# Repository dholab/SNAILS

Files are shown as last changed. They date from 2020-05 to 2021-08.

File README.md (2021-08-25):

# SNAILS v2.0
Since publishing, we have created a new version that is more mobile, efficient, and adaptable. This design also works with the more-common, upright Eppendorf pipette rather than the self-standing Ovation pipette. Please navigate to the SNAILS_v2 folder for the design.

SNAILS v2.0 assembly video: https://youtu.be/8Qm_oOv1cj8

# SNAILS v1.0
Slow Nucleic Acid Instrument for Long Sequences

SNAILS was created by Trent Prall and Emma Neumann. Its purpose is to improve ultralong read sequencing library preparation by reducing DNA shearing due to pipetting. 

preprint: https://www.biorxiv.org/content/10.1101/2020.09.18.302471v1

SNAILS v1.0 assembly video: https://youtu.be/rlQ-tXXK3FM

SNAILS v1.0 circuitry video: https://youtu.be/u-fqjHdVTUg

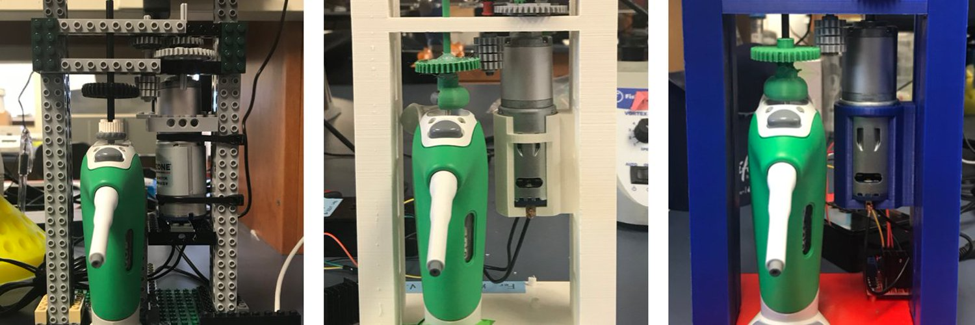
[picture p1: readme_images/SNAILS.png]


# Abstract
**Background** Oxford Nanopore Technologies’ instruments can sequence reads of great length. Long reads improve sequence assemblies by unambiguously spanning repetitive elements of the genome. Sequencing reads of significant length requires the preservation of long DNA template molecules through library preparation by pipetting reagents as slowly as possible in order to minimizing shearing. This process is time consuming and inconsistent at preserving read length as even small changes in volumetric flow rate can result in template shearing.

**Results** We have designed SNAILS (Slow Nucleic Acid Instrument for Long Sequences), a 3D-printable instrument that automates slow pipetting of reagents used in long read library preparation for Oxford Nanopore sequencing. Across six sequencing libraries, SNAILS preserved more reads exceeding one hundred kilobases in length and increased the average read length of its libraries over manual slow pipetting.

**Conclusions** SNAILS is a low-cost, easily deployable solution for improving sequencing projects that require reads of significant length. By automating the slow pipetting of library preparation reagents, SNAILS both increases the consistency and throughput of long read Nanopore sequencing.

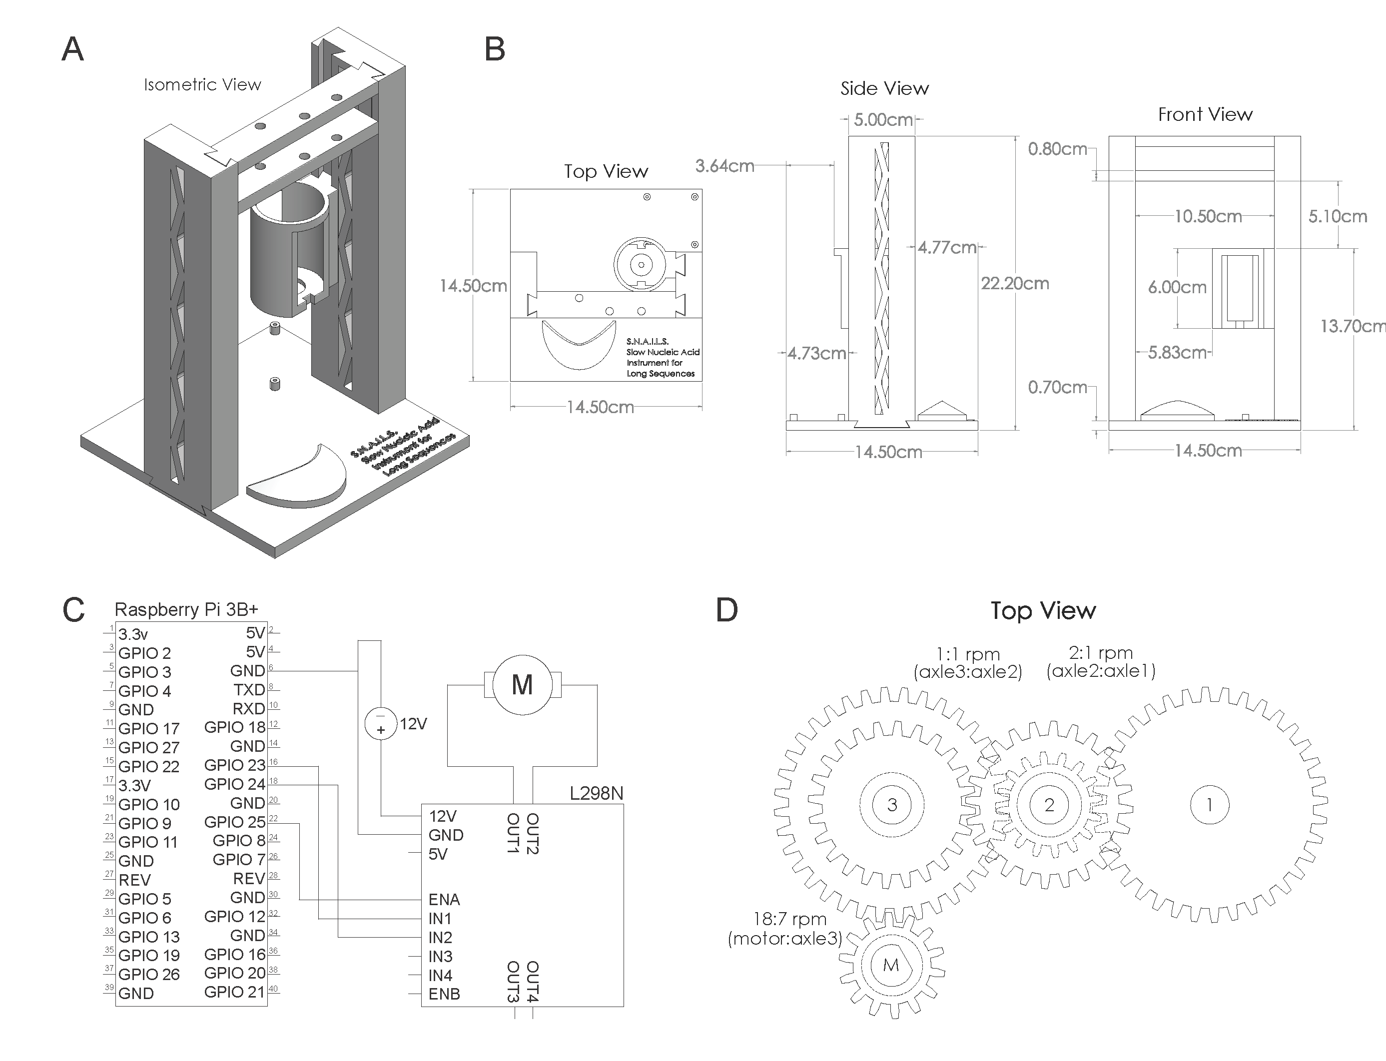
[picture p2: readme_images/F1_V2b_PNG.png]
F1_V2b_PNG


# Parts List
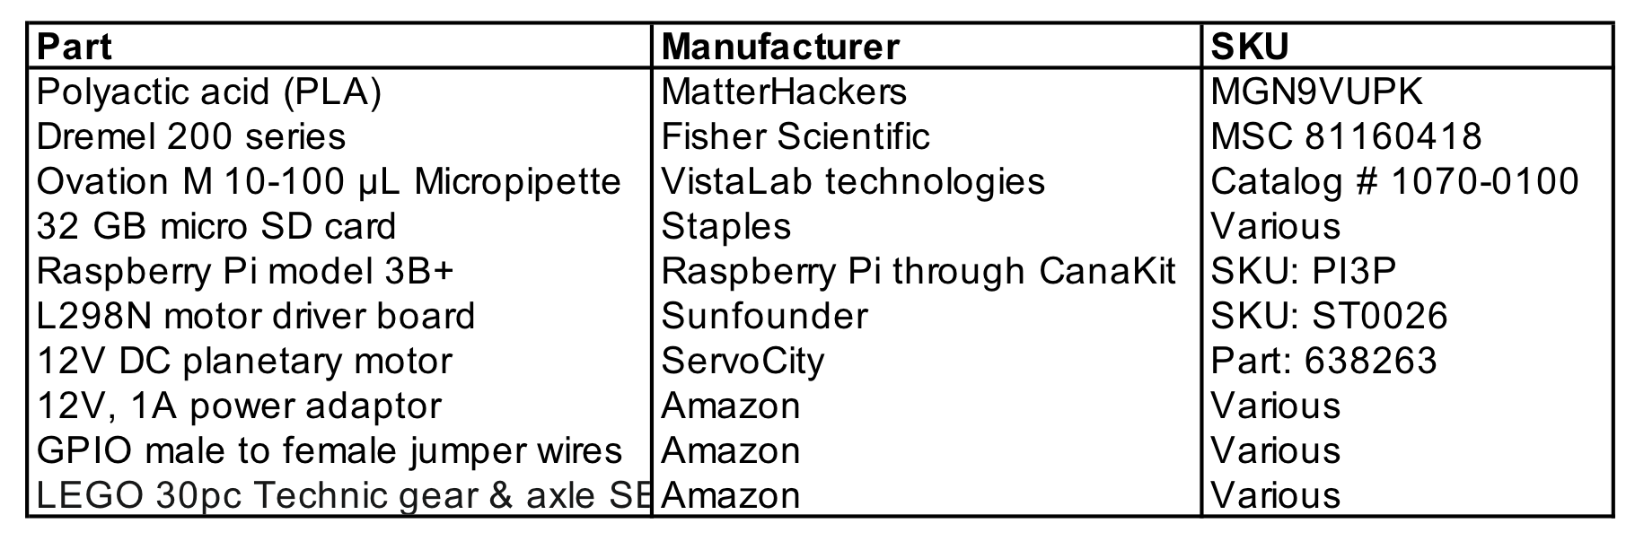
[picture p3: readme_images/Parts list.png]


# Printing Instructions
We used Ultimaker 3, S3, and S5 3D printers with the Ultimaker Cura program (https://ultimaker.com/software/ultimaker-cura). We recommend PLA for the printing material with the point set to 0.2 mm and infill at 20% for all the pieces. For the base, motor holder, and bridge, support material needs to be included, and changing the support density to 25 for a smoother print job is recommended. Additionally, we recommend that the base is printed on a separate build plate than the other pieces because it is so much thinner and by separating the pieces you increase the chances of a successful print job. More detailed, step-by-step printing instructions are directly below.

## Instructions for 3D printing SNAIL robot using an Ultimaker Cura
1. Connect to printer – this must be the first step because any and all settings altered will change anytime the printer is changed. You can connect to the printer through an IP address or network connection; follow the instructions on the screen. I used an Ultimaker 3 for the base and an Ultimaker S5 for the other four pieces; however, you can use any combination to print all the pieces. If you use a printer smaller than an S5 make sure it can still fit the towers and do not print all four pieces together. When printing multiple pieces at once, make sure the heights are about equal and the plate isn’t too full (Fig. 4 is the most crowded a plate should be). The base should be printed separate the other pieces because it is so much thinner than the others to increase the chances of a successful print. Once the printer is selected your screen should look like this:
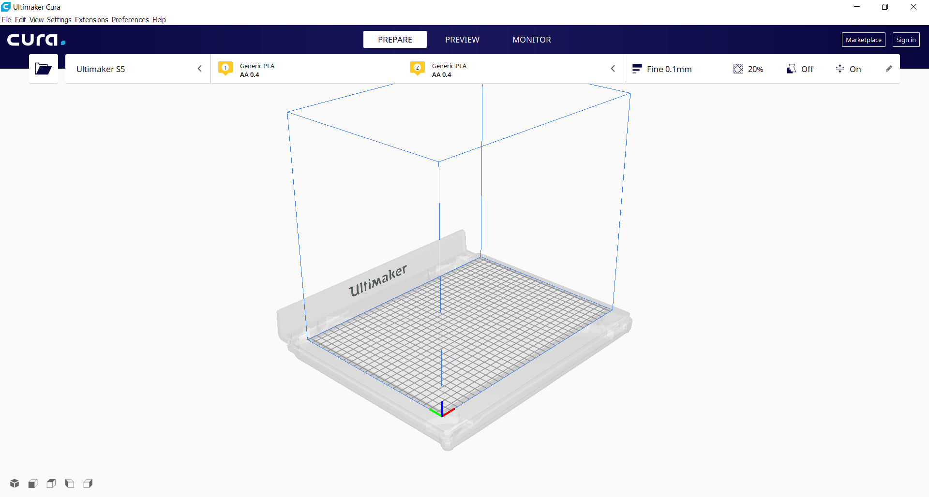
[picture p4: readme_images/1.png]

2. Open a file folder with all the STL files and drag those files into Cura onto the schematic of the printer.
3. Click on the part(s) and use the toolbar along the left side to rotate and move the parts (the next two pictures depict these movements) so that it lies flat on the printer and reduces support material. The pieces should be oriented as depicted below to produce the best prints.
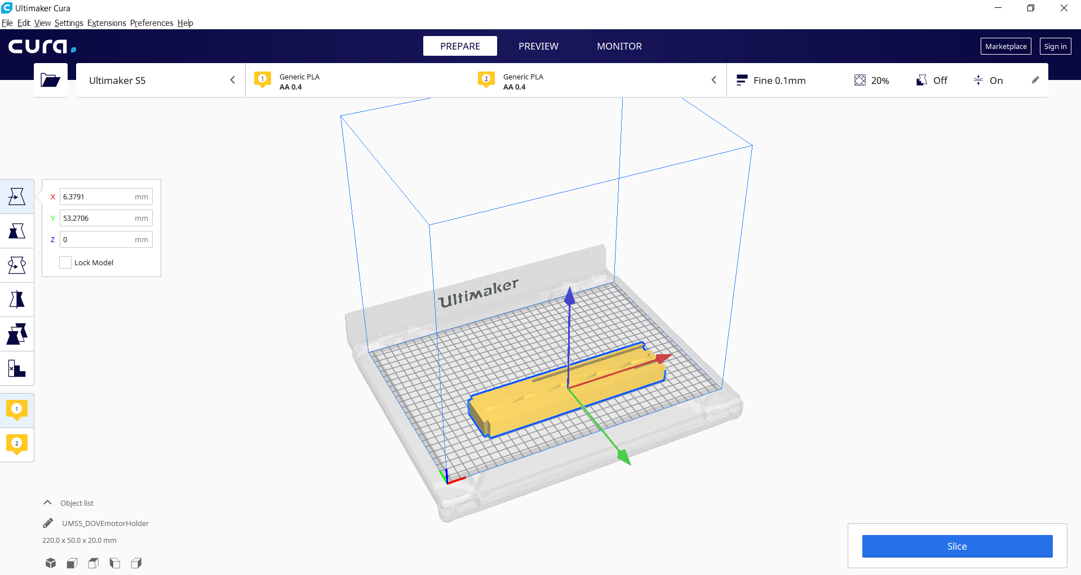
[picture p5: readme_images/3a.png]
3a

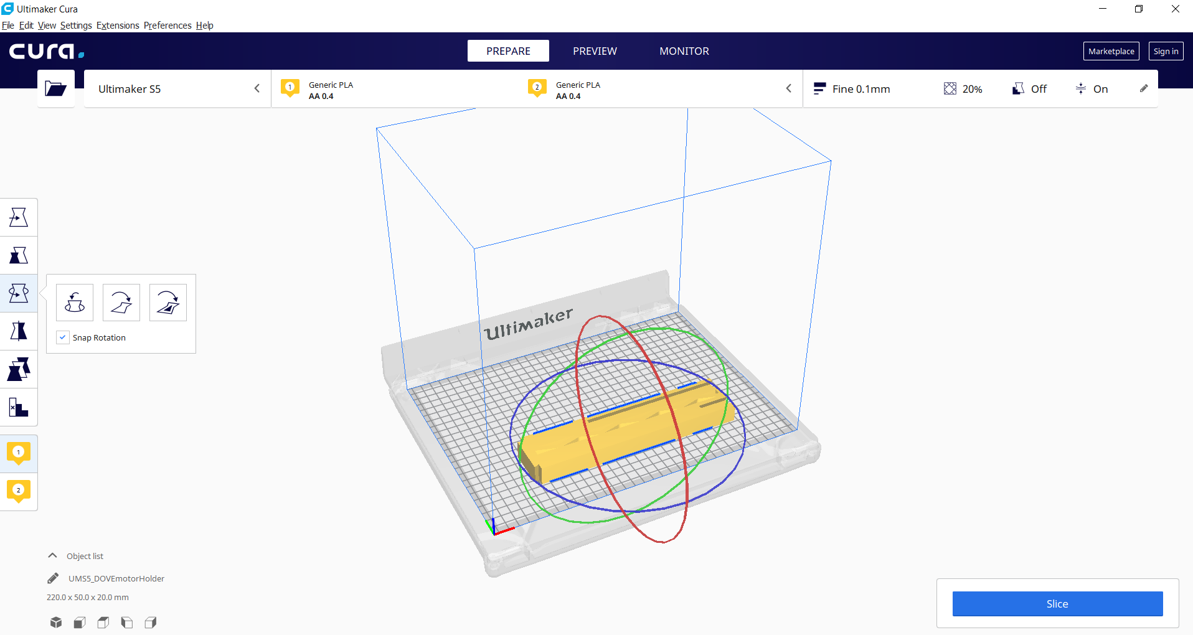
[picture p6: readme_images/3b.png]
3b

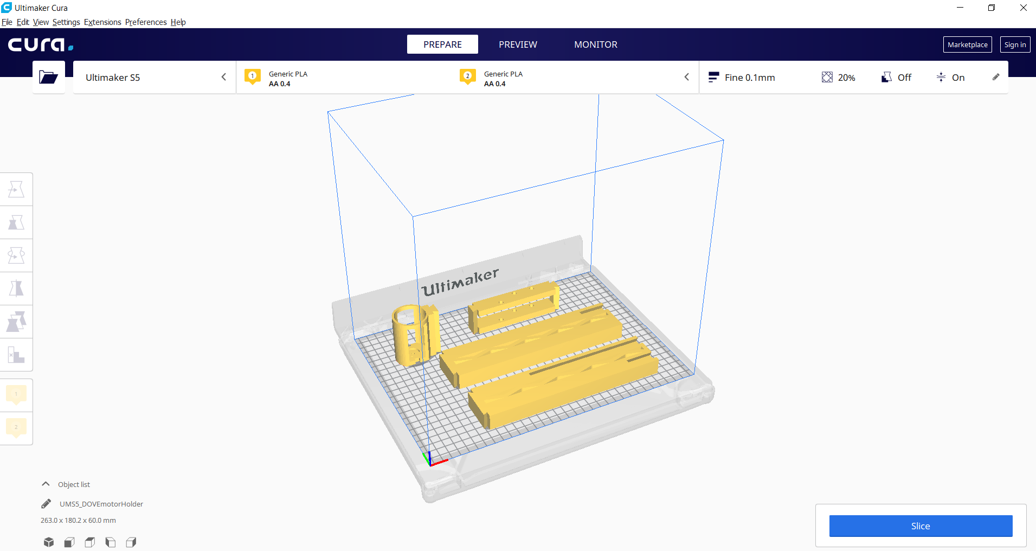
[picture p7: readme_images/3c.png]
3c

4. Set the material types to PLA and make sure it is communicating with the printer. If the material changes later, all settings will go back to the defaults.
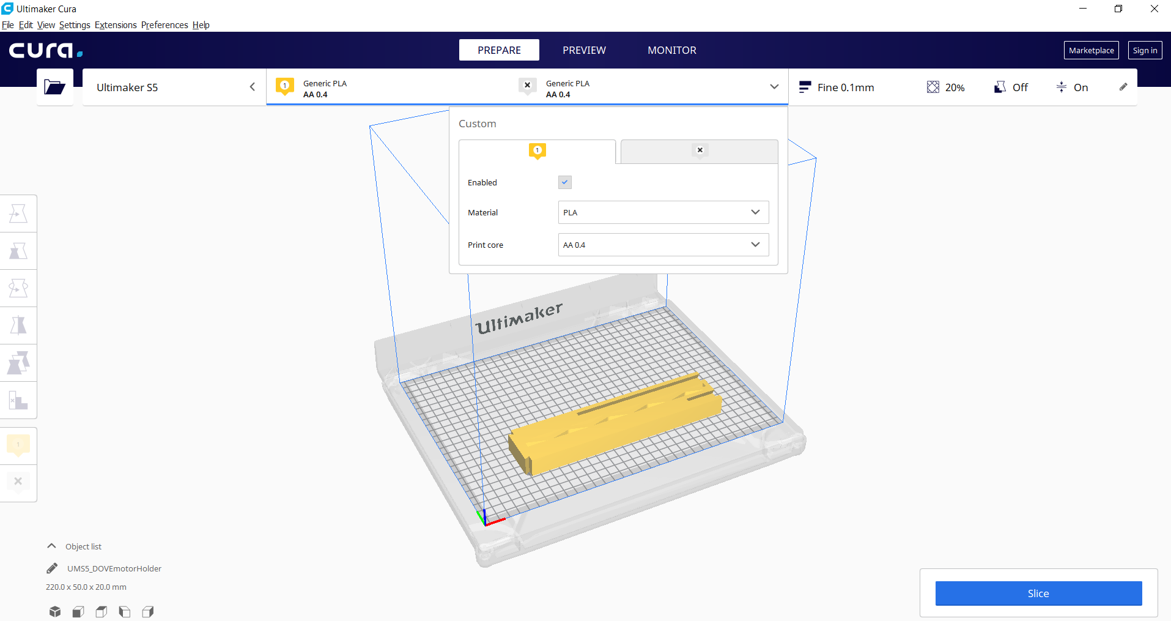
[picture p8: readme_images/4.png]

5. Go to Print Settings in the upper right. 
    - Layer Height: 0.2 (use 0.1 for the base)
    - Infill %: 20
    - Support: Check, Extruder 1 (if you only have one material in the printer this option will disappear, but if there are multiple materials make sure you choose the correct extruder)
    - Adhesion: Check
    - Custom -> Support -> Support Density: 25 (this setting isn’t crucial to change if it isn’t available on your machine, but it will make upper edges smoother)
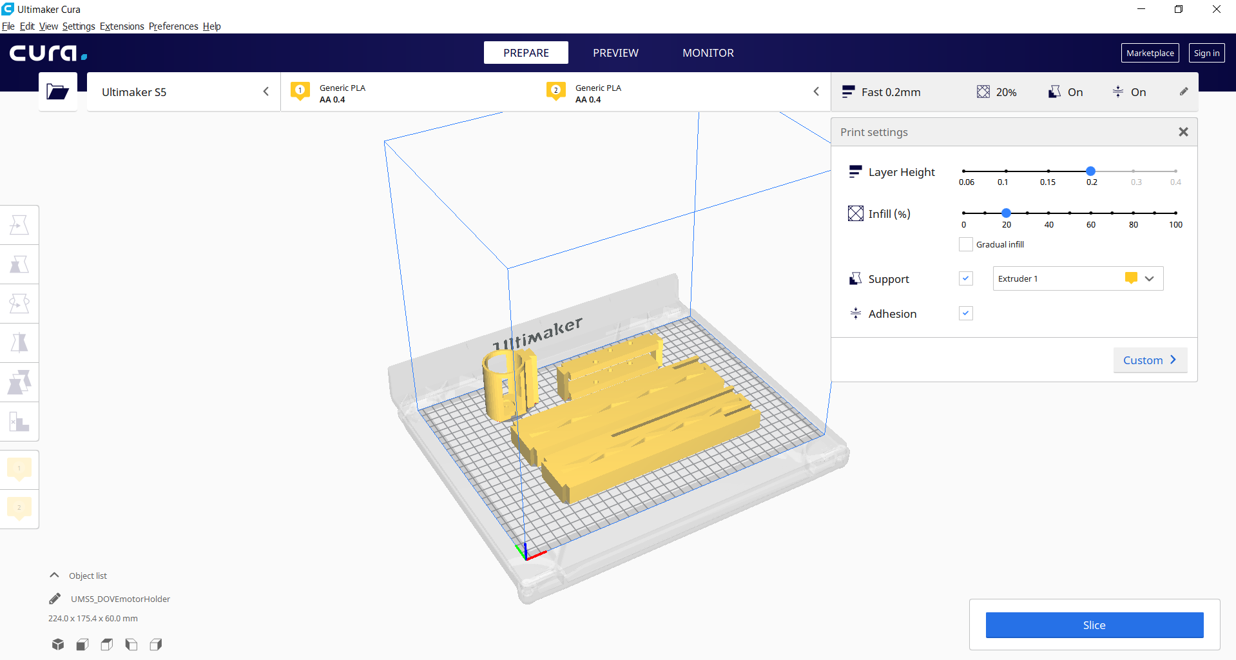
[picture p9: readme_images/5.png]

6. Click the blue Slice in the bottom right.
7. Click Preview at the top middle to verify the correct material and support material are produced. There is a scroll along the right side to view each layer. Change the color scheme to Line Type to more easily view the support.
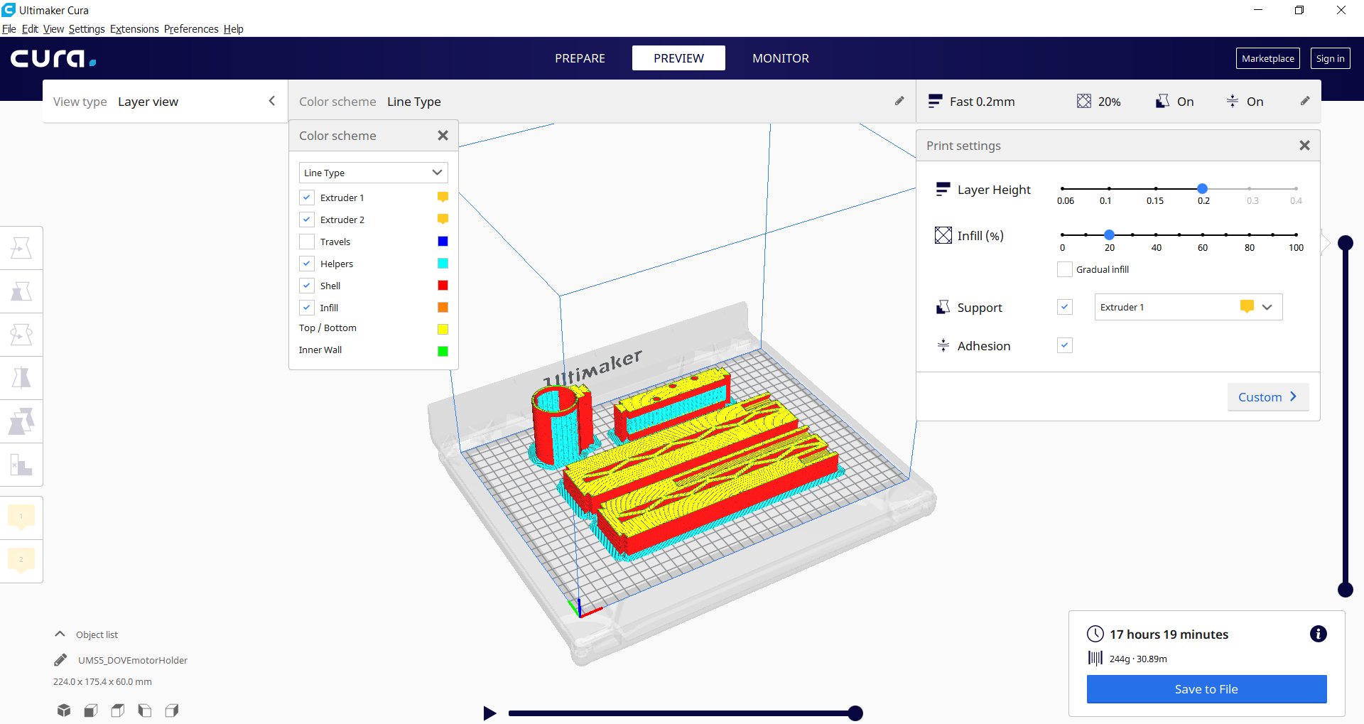
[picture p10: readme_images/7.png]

8. If everything looks correct, verify the printer is ready and click the blue, Print button in the bottom right. Make sure that the printer receives the print before leaving.

## Assembling
Once the 3D printing is complete, all of the support material must be removed and all of the pieces should be able to snap together. Due to the margin or error from an Ultimaker, it possible some of the pieces will need to be slightly shaved down with a dremel to fully remove the border support material. Regardless, the pieces intentionally are designed to fit tightly together to avoid moving while running so light taps from a mallet may help to make the joints fully flush.

# Circuitry
Raspbian v4.19 (https://www.raspberrypi.org/downloads/raspbian/) was installed using NOOBS v3.3.1 (https://www.raspberrypi.org/downloads/noobs/) to a 32 GB micro sd card and booted on a Raspberry Pi (rpi) model 3B+. Electronic components were assembled into a solderless circuit as depicted in Figure 1C. Briefly, the rpi GPIO pins 23,24, 25, and ground pin 6 were connected to IN1, IN2, ENA, and GND terminals of the L298N motor driver board (https://www.sunfounder.com/product-l298n-motor-driver-board-module.html), respectively. The positive and negative leads of a 12V DC power supply were connected to the 12V and GND terminals of the L298N motor driver, respectively. Finally, the two terminals of a 12V DC planetary motor ((https://www.servocity.com/12-rpm-hd-premium-planetary-gear-motor) were connected to the OUT1 and OUT2 terminals of the L298N motor driver.
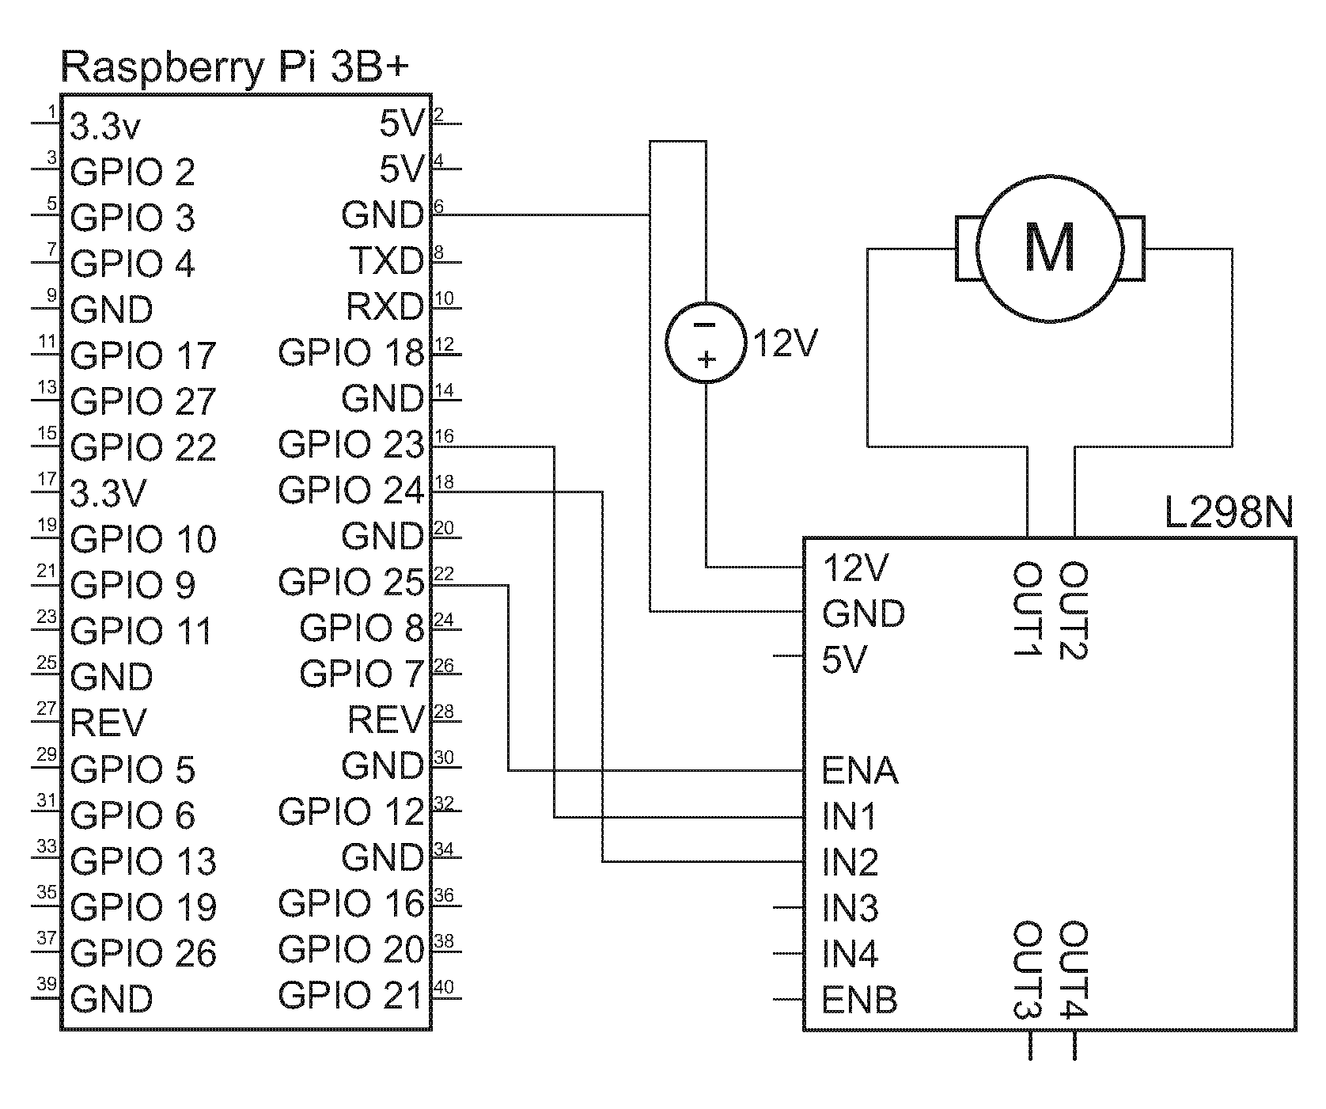
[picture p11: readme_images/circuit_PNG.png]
circuit_PNT


# Results
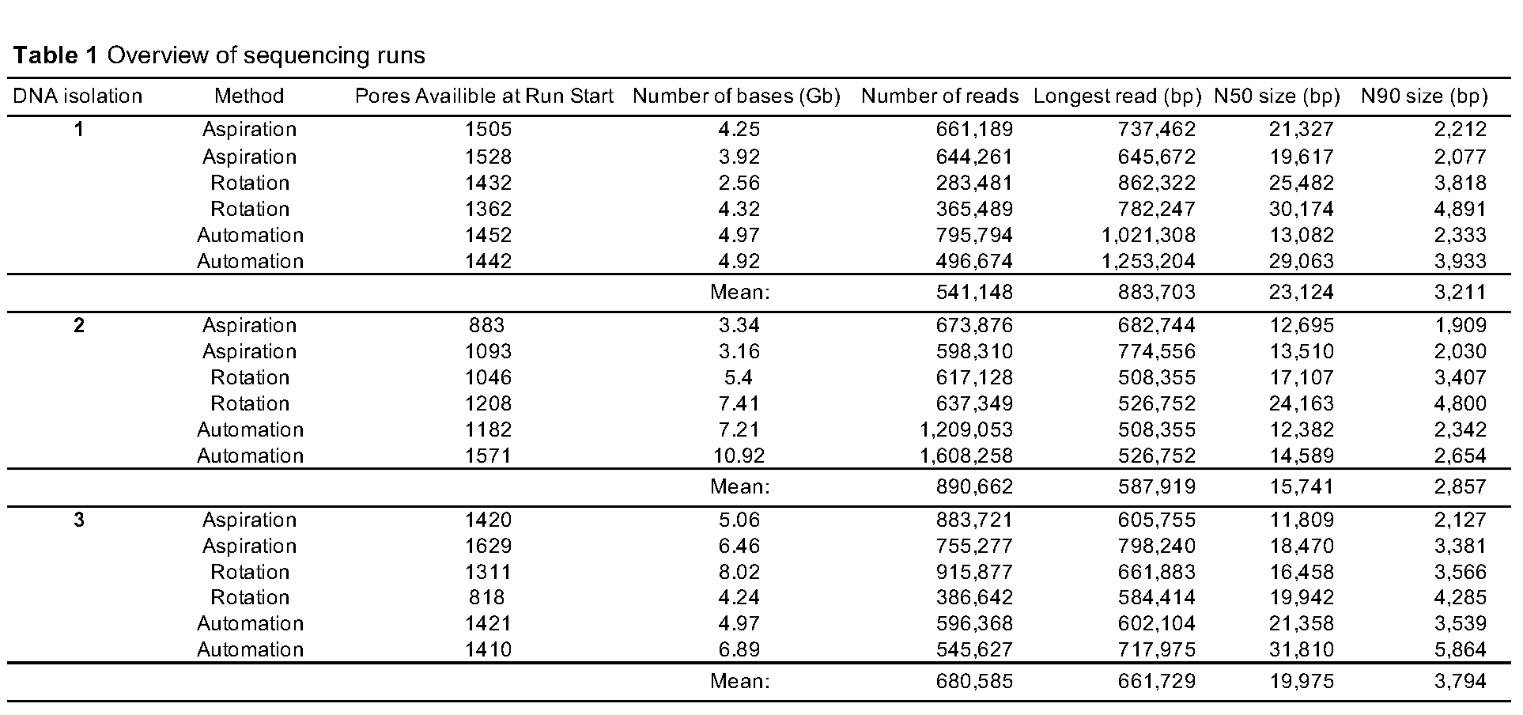
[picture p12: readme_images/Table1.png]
Table1

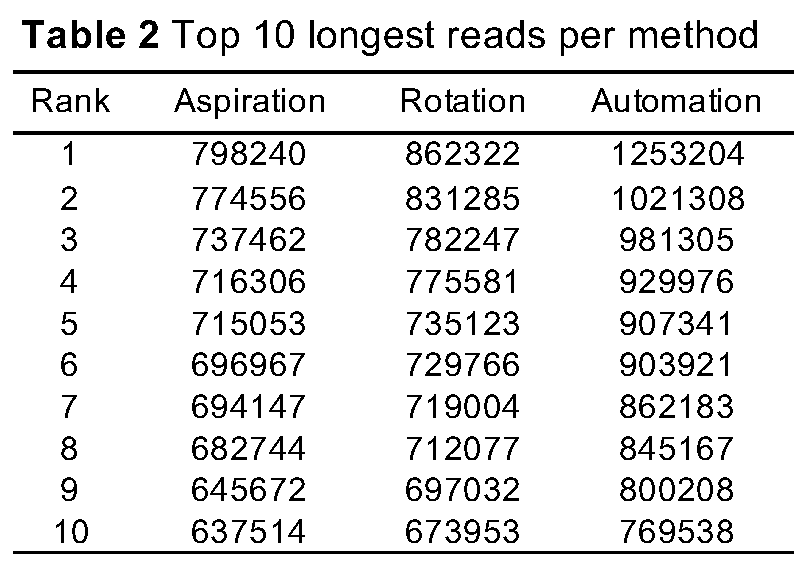
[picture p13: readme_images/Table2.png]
Table2


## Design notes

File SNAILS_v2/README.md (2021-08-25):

# SNAILS v2.0

assembly video: https://youtu.be/8Qm_oOv1cj8

SNAILS v2.0 works very similarly to the SNAILS v1.0 but with a much sleeker and efficient design. This design utilizes an upright Eppendorf pipette rather than the self-standing Ovation pipette to make it more accessible. It also is much more adaptable by being mobile and the gear ratio is easier to adjust.

The main difference is that the new design is intended to be mounted on an arm of some sort. This can be as simple as a ring stand clamp or as adaptable as a microphone/camera stand; whatever works for your application and budget.

## 3D printing
There is less 3D printing required for this design and fewer parts. There is also no need to use Lego parts like we suggested in v1.0.

## Circuitry
The circuitry is also more efficient and uses a Raspbery Pi Zero.

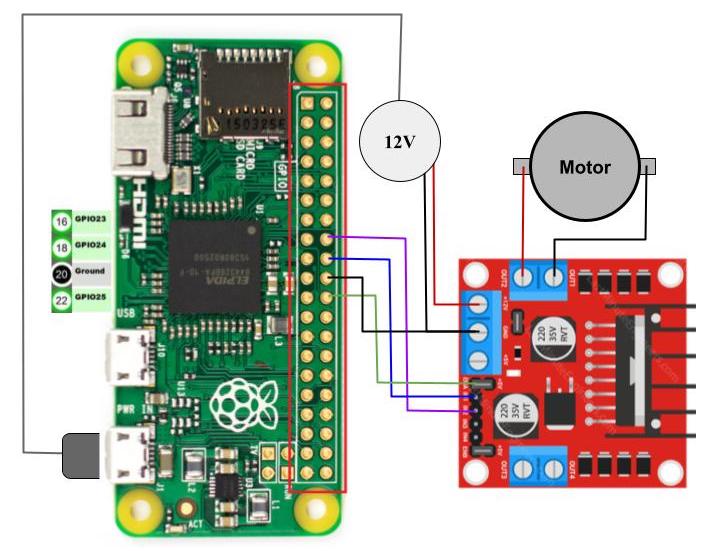
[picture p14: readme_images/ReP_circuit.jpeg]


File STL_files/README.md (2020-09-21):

# STL Files

These STL files are 3D object files that can be used to 3D print all the SNAILS parts. Printing instructions are on the main SNAILS page.

## Gears and Axles
All gear and axle STL files are provided. We recommend using the cap.gear.axle assembly over printing each part individually for the axle above the pipette. The 3D printed gears and axles usually work; however, depending on the quality of your 3D printer, they may not be as accurate or durable as desired. Therefore, we recommend using Lego gears and axles for everything except the axle above the pipette (use the cap.gear.axle assembly) and the gear that fits over the motor (14gear1). You can use a combination of 3D printed gears and Lego gears, as they are designed to fit together.

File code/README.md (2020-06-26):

# Code

These five programs are specifically designed for the Oxford Nanopore Technology SQK-RAD004 Rapid Sequencing Library Preparation Kit and can be ran through a raspberry pi to control the SNAILS liquid handling robot as described on the main SNAILS page.

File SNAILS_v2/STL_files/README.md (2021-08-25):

# STL Files

These STL files are 3D object files that can be used to 3D print all the SNAILS parts. Printing instructions are on the main SNAILS page. There is significantly less 3D printing required for v2.0 and no Lego gears are required.

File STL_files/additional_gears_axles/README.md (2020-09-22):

# Additional Gears and Axles
These are the gears and axles. These gears are sized identically to Lego Technic gear sizes. We recommend you replace with Lego technic parts for ease of assembly (see parts list)

LEGO 30pc Technic gear & axle SET: https://www.amazon.com/LEGO-Technic-Mindstorms-robot-hobby/dp/B01LW6Z8D4/ref=sr_1_18?dchild=1&keywords=Lego+technic+axle&qid=1600739157&sr=8-18

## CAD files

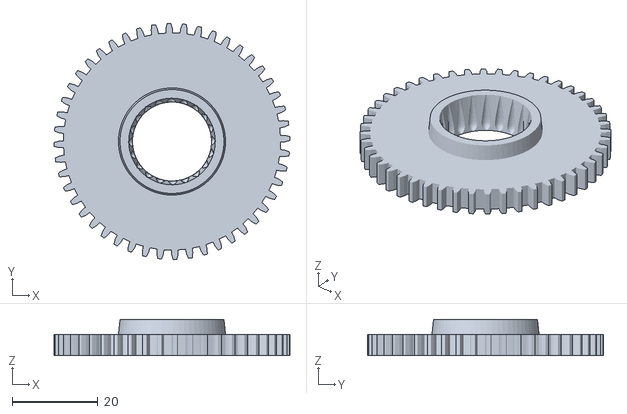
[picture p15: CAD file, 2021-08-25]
SNAILS_v2/STL_files/gear_cap_assembly.STL
55.0 x 55.0 x 8.50

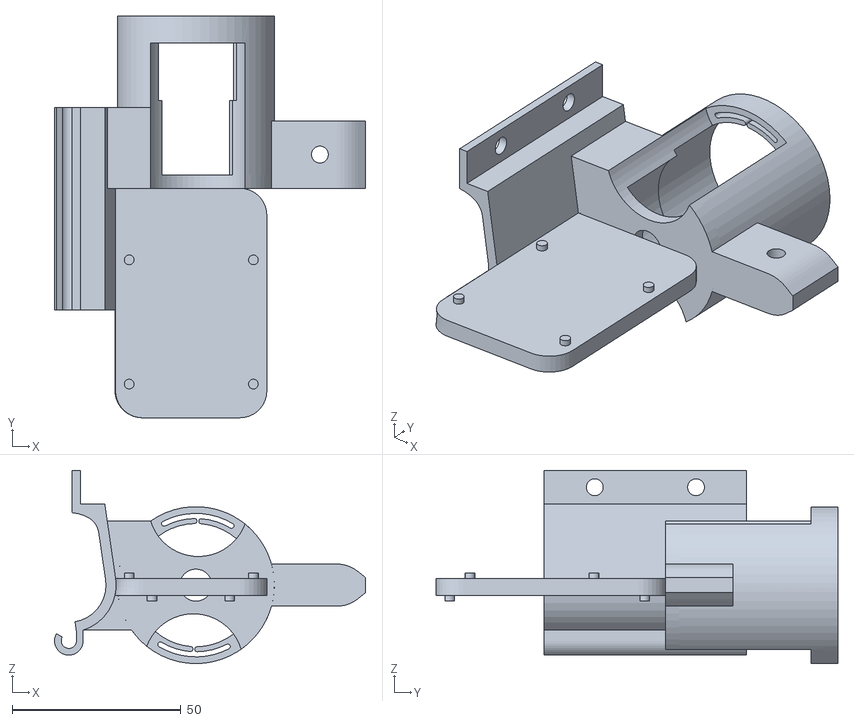
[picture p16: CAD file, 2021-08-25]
SNAILS_v2/STL_files/mount_assembly.STL
92.1 x 119.0 x 57.2

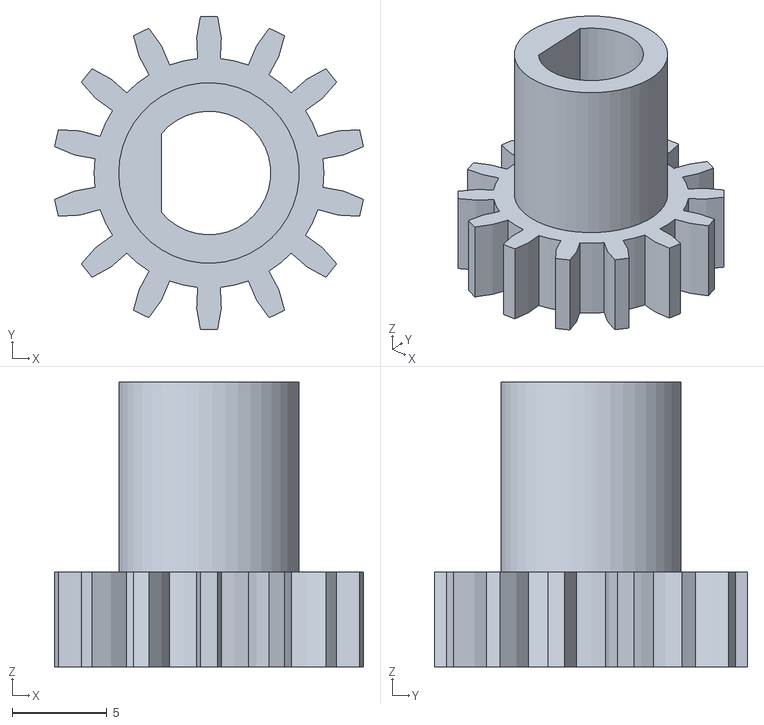
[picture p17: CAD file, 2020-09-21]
STL_files/14gear1.STL
16.3 x 16.5 x 15.0

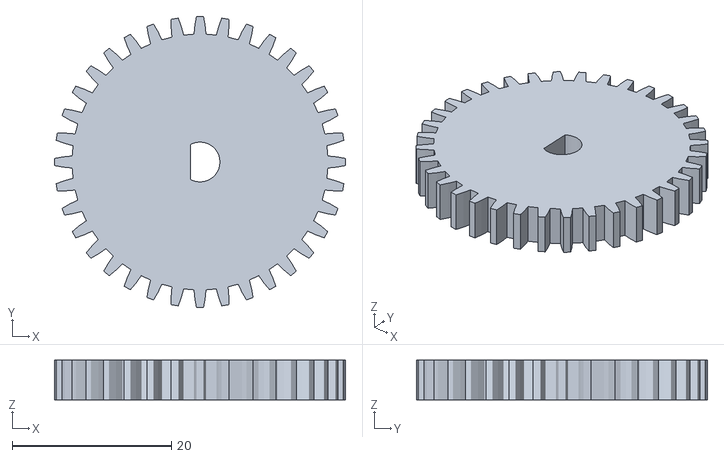
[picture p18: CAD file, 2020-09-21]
STL_files/additional_gears_axles/36gear1.STL
36.5 x 36.5 x 5.00

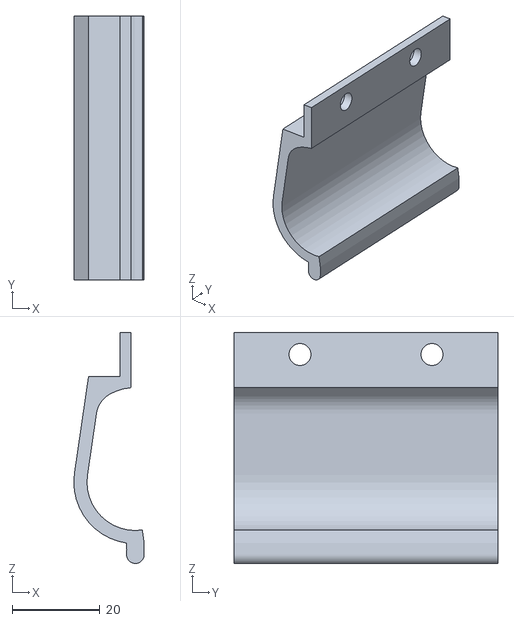
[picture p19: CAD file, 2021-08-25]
SNAILS_v2/STL_files/clip_side1_b.STL
16.0 x 60.0 x 52.5

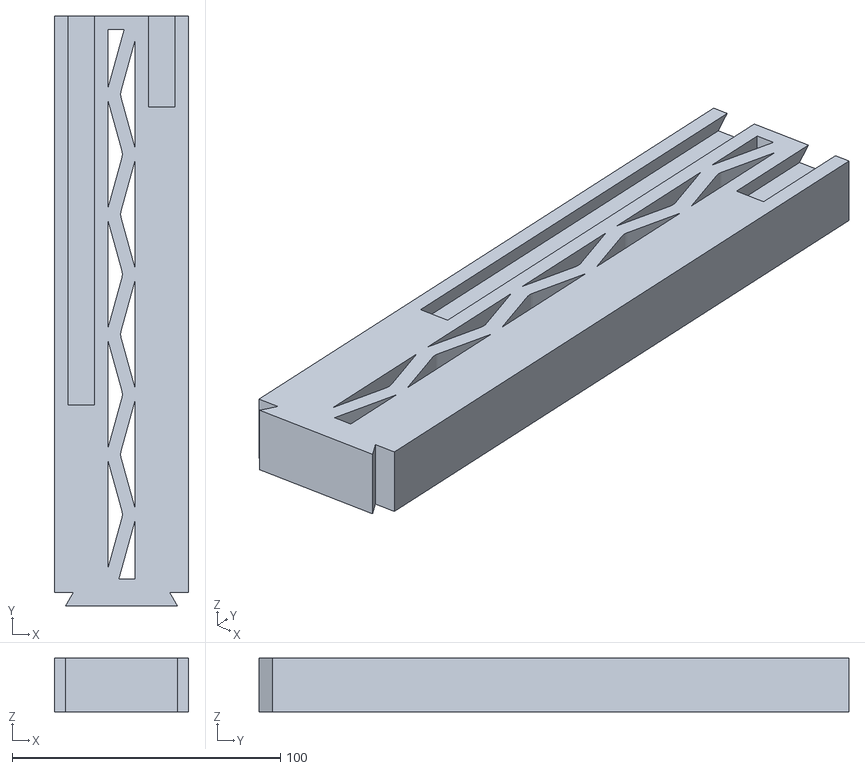
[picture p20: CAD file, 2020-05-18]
STL_files/2dove tail tower.STL
50.0 x 220.0 x 20.0

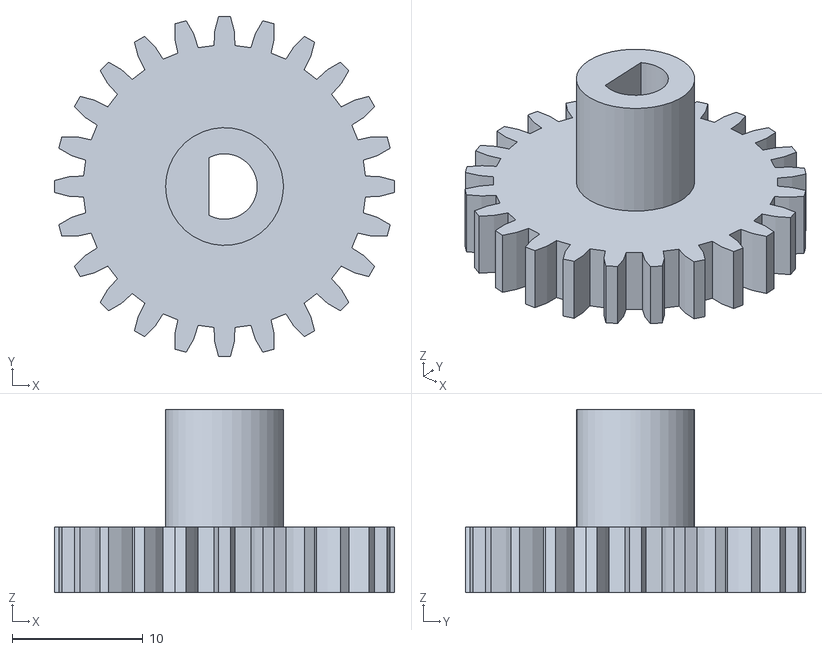
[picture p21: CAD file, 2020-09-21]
STL_files/additional_gears_axles/24gear1.STL
26.0 x 26.0 x 14.0

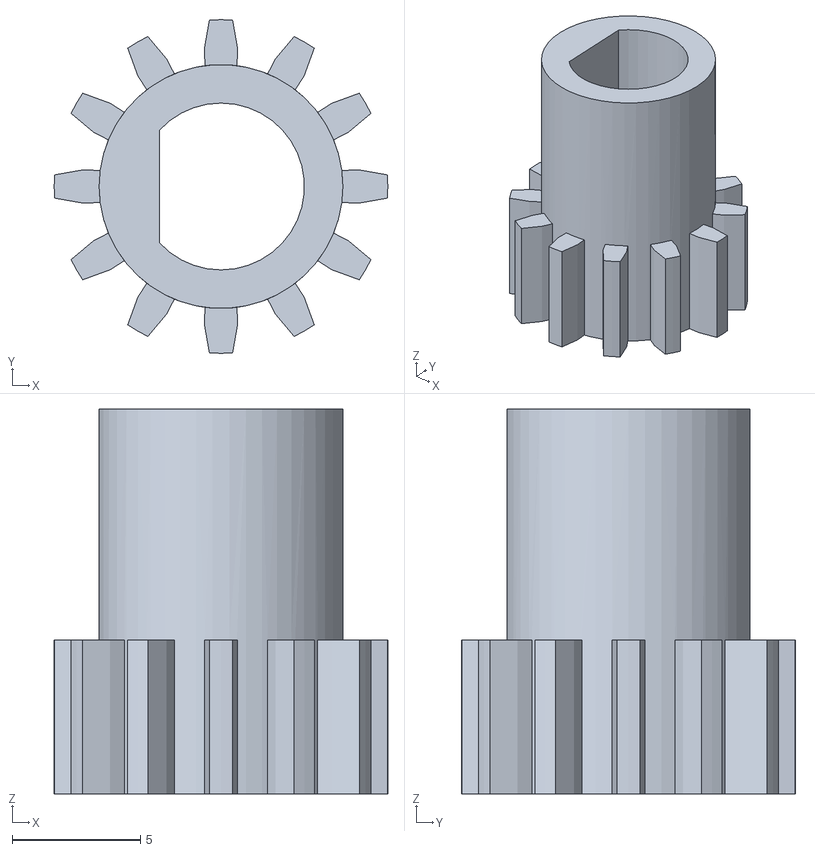
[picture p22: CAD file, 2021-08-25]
SNAILS_v2/STL_files/12gear.STL
13.0 x 13.0 x 15.0

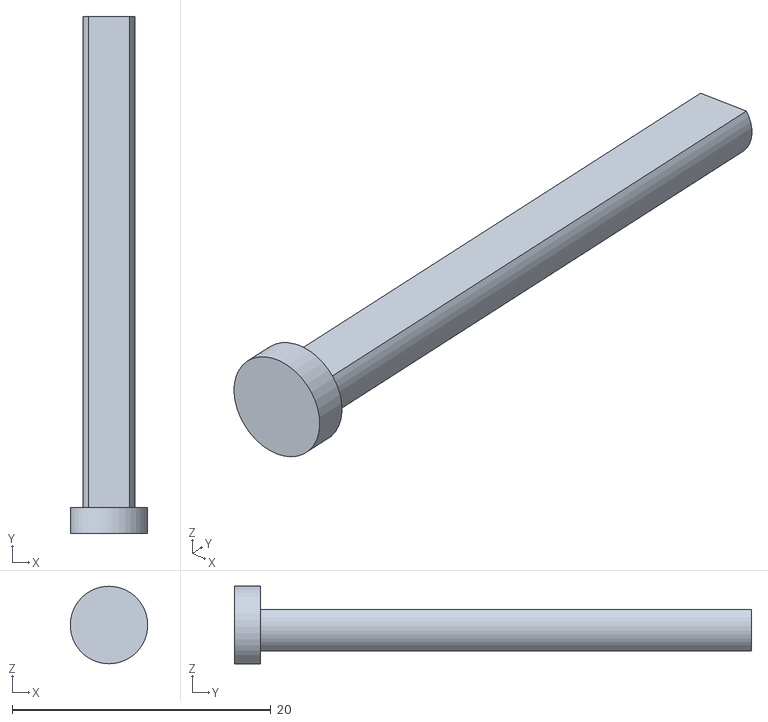
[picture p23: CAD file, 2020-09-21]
STL_files/additional_gears_axles/axel.STL
5.99 x 40.0 x 6.00

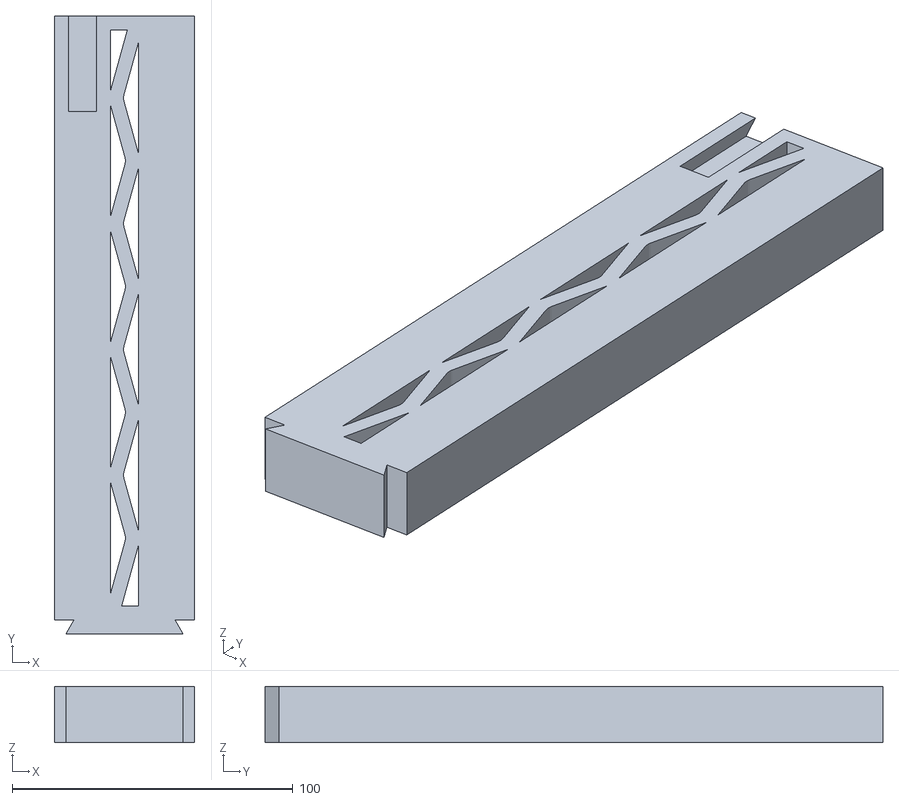
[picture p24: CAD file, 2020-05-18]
STL_files/dove tail tower.STL
50.0 x 220.0 x 20.0

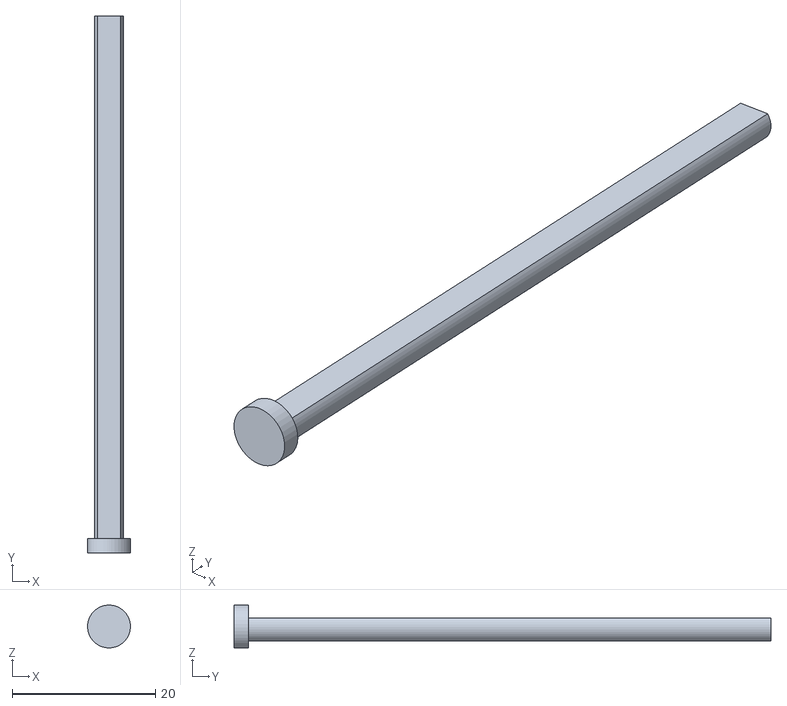
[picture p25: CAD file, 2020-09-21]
STL_files/additional_gears_axles/axel2.STL
5.99 x 75.0 x 6.00

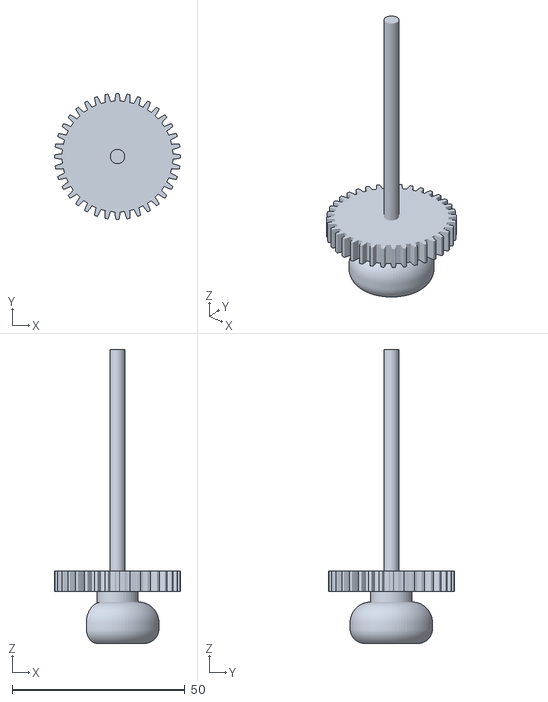
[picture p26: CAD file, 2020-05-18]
STL_files/cap.gear.axel.STL
36.5 x 36.5 x 85.0

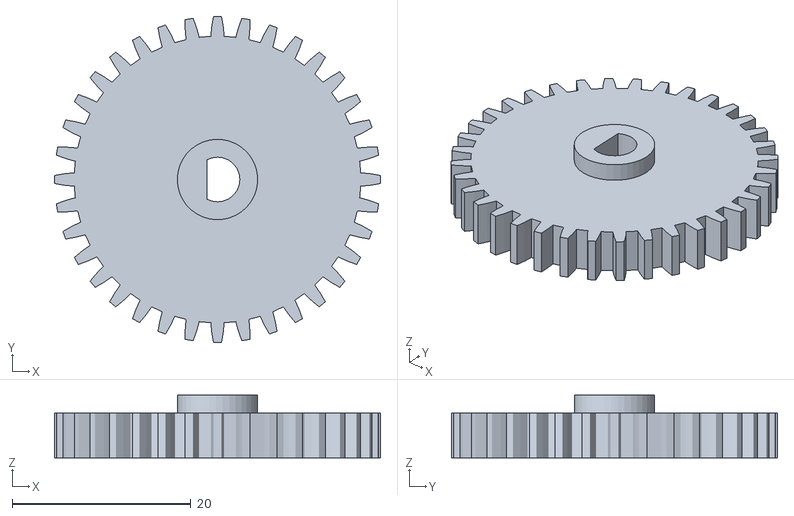
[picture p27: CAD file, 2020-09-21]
STL_files/additional_gears_axles/36gear2.STL
36.5 x 36.5 x 7.00

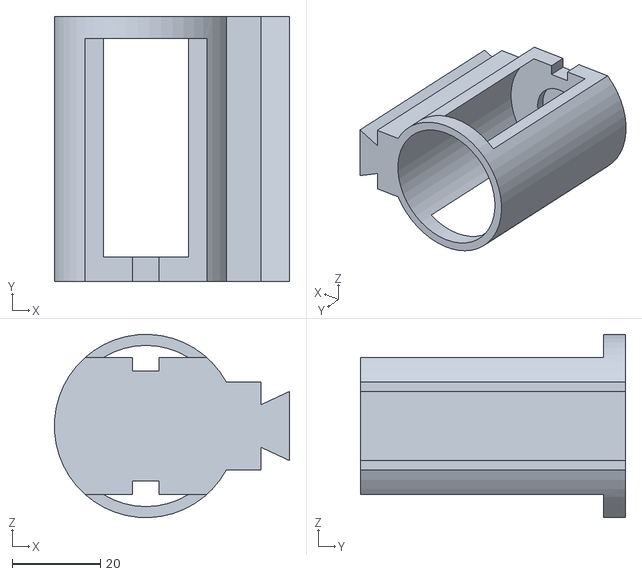
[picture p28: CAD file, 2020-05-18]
STL_files/DOVEmotorHolder.STL
53.2 x 60.0 x 41.5

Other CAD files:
STL_files/additional_gears_axles/24gear2.STL
STL_files/DOVEbridge.STL
STL_files/additional_gears_axles/16gear1.STL
STL_files/DOVEbase.STL

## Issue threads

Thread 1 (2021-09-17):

### ISSUE TITLE
Really cool product -can we have a video?

### ISSUE THREAD

**Issue by Kirk3gaard** [dholab/SNAILS#1]
Hi 

This is a really cool idea. Any chance that you could post  a link to a video with the SNAILS in action? 

+ I seem unable to find the mention of the pipettor itself in the description and where to get it like the links you have for the motors etc.

Best regards 
Rasmus

**Comment by TrentPrall** [comment]
Hi Rasmus,

Thanks for reaching out to us. We have updated our GitHub repository to
include more information on parts and assembly. We are currently working on
an instructional video for assembly that will be online shortly. Below is a
complete parts list.

The design uses an Ovation M 10-100 ul Micropipette
https://vistalab.com/product/mechanical-volume-adjust/
Catalog # 1070-0100
If you have any questions or need assistance setting up an instrument
please feel free to ask.

Best,
Trent
O'Connor Lab
University of Wisconsin, Madison

**Comment by neuropathbasel** [comment]
Hi Trent,
Many thanks for the publication and this github page detailing your invention.
However, so far I am not really not sure I do understand the setup and how it is used for pipetting.
I would like to support Rasmus' request for a video of the SNAILS in action.
Many thanks & best wishes
Claus

**Comment by TrentPrall** [comment]
Hey @neuropathbasel and @Kirk3gaard,

Sorry for the delay but we have finally created assembly videos that are linked on the main page. Hopefully that helps you deploy if you're still interested in trying them out.

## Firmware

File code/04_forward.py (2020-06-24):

#!/usr/bin/env python

# this modules are necessary to run the raspberry pi and interact with the general purpose input/output (GPIO) pins
import RPi.GPIO as GPIO
# this module is important for setting duration and pauses in the code
import time

# Set up pins
MotorPin1   = 17
MotorPin2   = 18
MotorEnable = 27

# this is the message that will print when the program is run and gives instructions to the user
def print_message():
	print ("========================================")
	print ("|                Move pipette up       |")
	print ("|    ------------------------------    |")
	print ("|     Motor pin 1 connect to GPIO0     |")
	print ("|     Motor pin 2 connect to GPIO1     |")
	print ("|     Motor enable connect to GPIO2    |")
	print ("|                                      |")
	print ("|         Controlling a motor          |")
	print ("|                                      |")
	print ("|                          O'Connor Lab|")
	print ("========================================\n")
	print ('Program is running...')
	print ('Please press Ctrl+C to end the program...')
	raw_input ("Press Enter to begin\n")

def setup():
	# Set the GPIO modes to BCM Numbering
	GPIO.setmode(GPIO.BCM)
	# Set pins to output
	GPIO.setup(MotorPin1, GPIO.OUT)
	GPIO.setup(MotorPin2, GPIO.OUT)
	GPIO.setup(MotorEnable, GPIO.OUT, initial=GPIO.LOW) # sets the motor to off at the start

# Define a motor function to spin the motor
# direction should be 
# 1(clockwise), 0(stop), -1(counterclockwise)
# if the wires ever get switched, clockwise will become counterclockwise and vise versa
def motor(direction):
	# Clockwise
	if direction == 1:
		# Set direction
		GPIO.output(MotorPin1, GPIO.HIGH)
		GPIO.output(MotorPin2, GPIO.LOW)
		# Enable the motor
		GPIO.output(MotorEnable, GPIO.HIGH)
		print ("Clockwise")
	# Counterclockwise
	if direction == -1:
		# Set direction
		GPIO.output(MotorPin1, GPIO.LOW)
		GPIO.output(MotorPin2, GPIO.HIGH)
		# Enable the motor
		GPIO.output(MotorEnable, GPIO.HIGH)
		print ("Counterclockwise")
	# Stop
	if direction == 0:
		# Disable the motor
		GPIO.output(MotorEnable, GPIO.LOW)
		print ("Stop")

def main():
	print_message() # prints the message written above

	# Define a dictionary to make the script more readable
	# CW as clockwise, CCW as counterclockwise, STOP as stop
	directions = {'CW': 1, 'CCW': -1, 'STOP': 0}
	iteration = 1
	while iteration < 6:

		if iteration < 6:
			# Clockwise
			motor(directions['CW'])
			time.sleep(180)
		else:
			print ("Error")

# stops the motor and unassigns the GPIO pins
def destroy():
	# Stop the motor
	GPIO.output(MotorEnable, GPIO.LOW)
	# Release resource
	GPIO.cleanup()    

# If trying to running this script directly, do:
if __name__ == '__main__':
	setup()
	try:
		main()
		print ("FRA Mix Completed")
		
	# When 'Ctrl+C' is pressed, the child program destroy() will be execut
	except KeyboardInterrupt:
		destroy()
